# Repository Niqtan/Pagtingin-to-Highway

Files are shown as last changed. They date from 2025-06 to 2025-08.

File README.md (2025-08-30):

# Pagtingin (Obstacle Detecting Glasses)

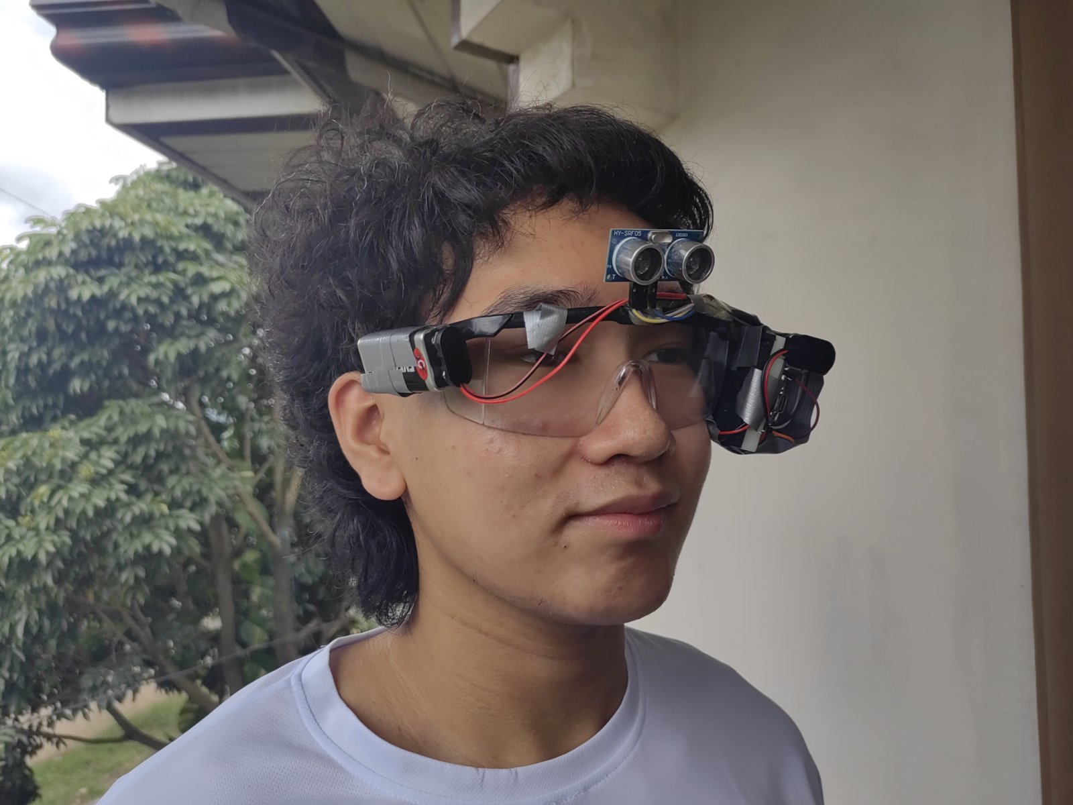
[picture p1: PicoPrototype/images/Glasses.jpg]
Project Wearable

Image 1. Pagtingin Prototype V1

## Prototype Demonstration
https://www.youtube.com/watch?v=mGvRfI-a0dM

# STATUS
Unfortunately, the ordered PCB did not end up working.

## Project Aims

The Pagtingin obstacle detecting glasses aims to help visually impaired people to easily detect obstacles in front of them through innovative glasses. While traditional walking sticks indeed help in detecting obstacles on the ground, they often fail to identify objects at chest or head level, such as low-hanging branches, open cabinets, or protruding signs. 

Hence, Pagtingin aims to aid this limitation and ensure a safe journey of navigation. Whether indoors or outdoors, the device will be able to identify potential hazards through a Time-of-Flight sensor and send real-time audio feedback, which helps users to be much more confident and safe in the user's day-to-day lives.

(+ I wanna try walking blindly sometimes)

Blind person walking happily

Courtesy of Freepik

## PCB Version
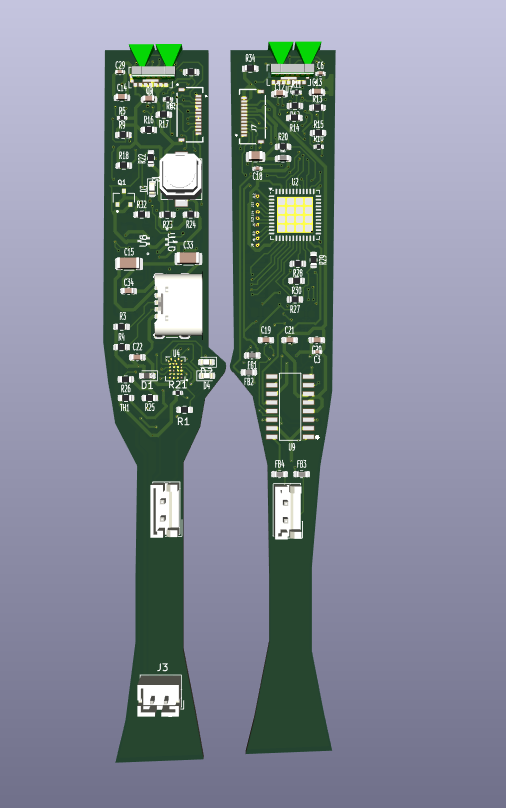
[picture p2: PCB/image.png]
PCB front view

Image 2. PCB Front View

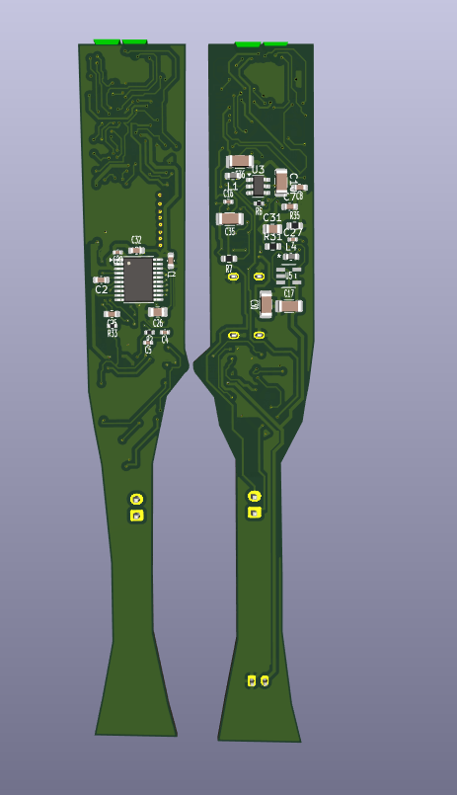
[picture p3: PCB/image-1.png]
PCB Back View

Image 3. PCB Back View

## Panelized Version

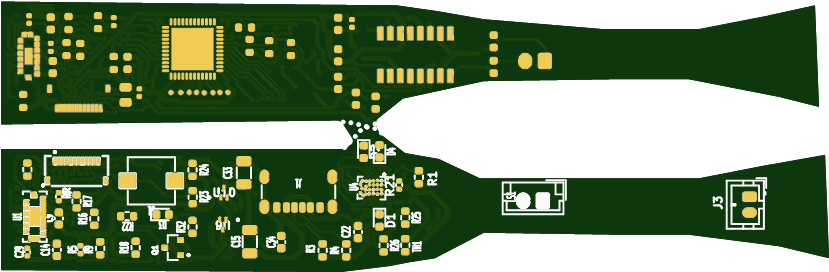
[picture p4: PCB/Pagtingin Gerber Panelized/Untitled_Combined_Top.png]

Image 3. Panelized PCB Front View

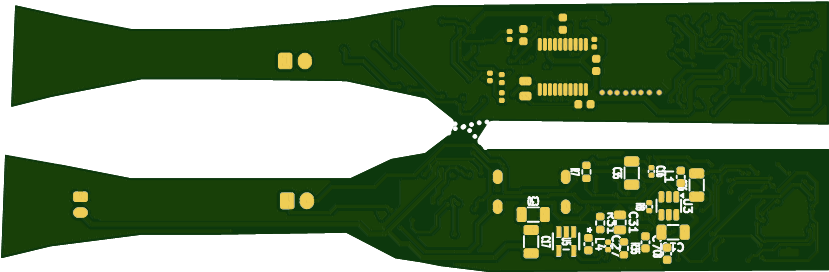
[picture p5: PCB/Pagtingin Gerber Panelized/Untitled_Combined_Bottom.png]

Image 4. Panelized PCB Back View

## CAD

### Glasses Frame

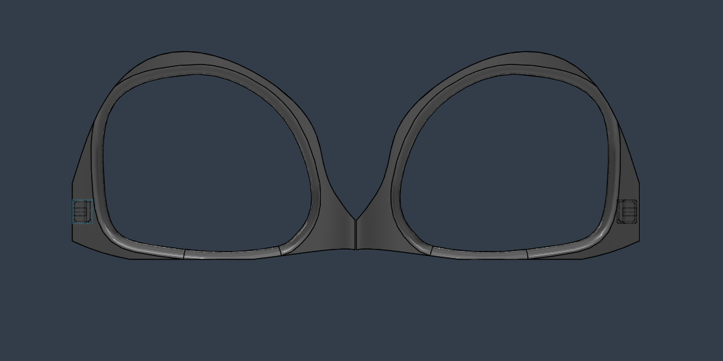
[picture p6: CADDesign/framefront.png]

Image 5. Glasses Frame Front View

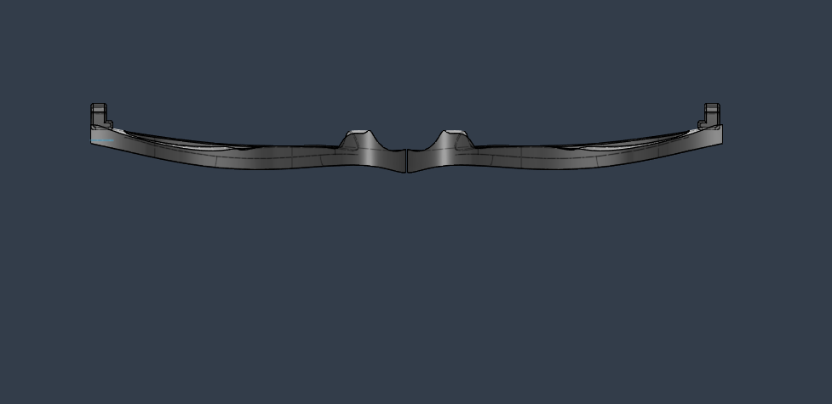
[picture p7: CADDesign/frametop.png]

Image 6. Glasses Frame Top View

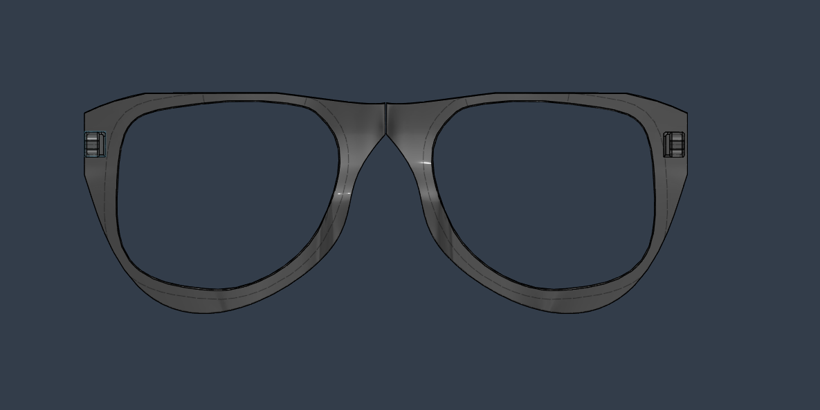
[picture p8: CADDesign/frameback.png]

Image 7. Glasses Frame Back View

### Temples

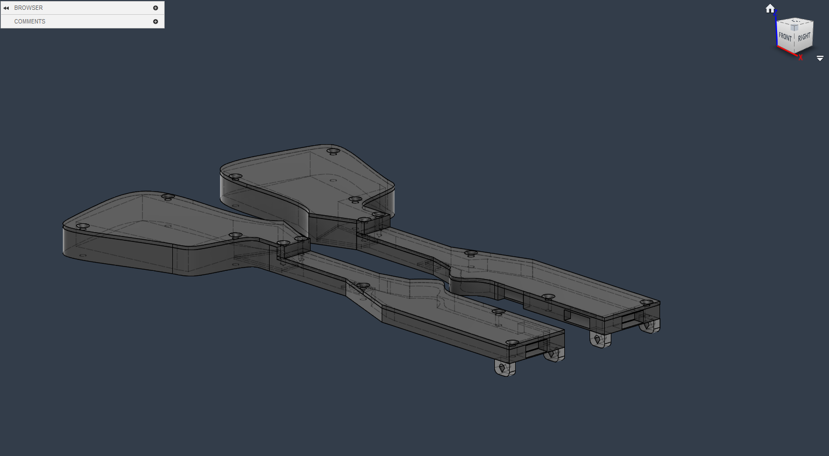
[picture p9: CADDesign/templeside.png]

Image 8. Glasses Temple Side View

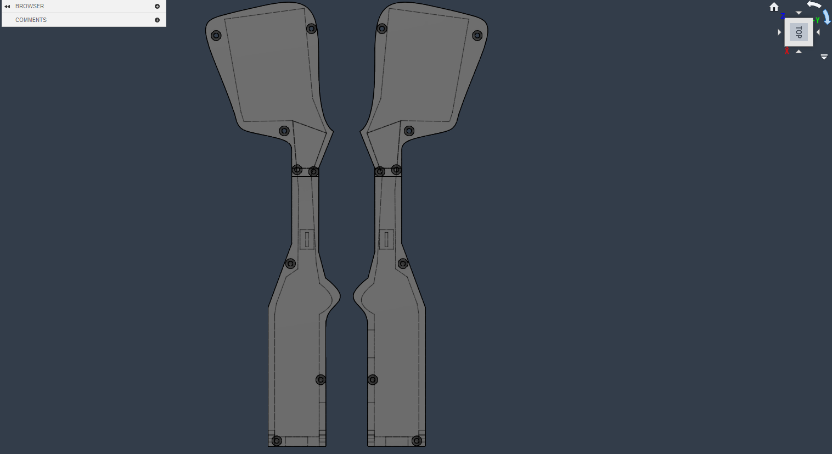
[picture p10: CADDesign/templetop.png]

Image 9. Glasses Temple Top View

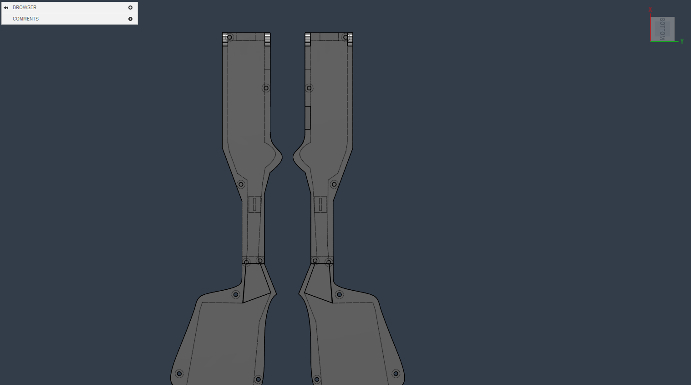
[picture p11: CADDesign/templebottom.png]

Image 10. Glasses Temple Bottom View

## 3D Printing
In terms of 3D printing, it might be better to print this in resin since the glasses frame will require precise dimensions. You may be able to print this in FDM, but it is recommended for the parameters to be as precise as possible.

## BOM
[PagtinginFinal.csv](PagtinginFinal.csv)

## Firmware
Still in progress. You may see previous prototypes in the folder for previous version's firmware. But for the firmware, I am planning to use the ESP-IDF in programming it. I chose the ESP-IDF because it allows full control over the ESP32-PICO-D4's peripherals and such. (also because I wanna challenge myself)

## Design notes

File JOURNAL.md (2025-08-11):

---
title: "Pagtingin"
author: "Niq Suguitan"
description: "A vision without action is called a daydream; but then again, action without a vision is called a nightmare."
created_at: "2025-30-25"
---

DISCLAIMER: I had been working on this project even before Highway. I had a prototype V1 beforehand. However, most of the CAD and PCB Making happened during the duration of Highway.

| Date started: March 17, 2025 

Total hours spenta: 
128 Hours

P.S. These were all my notes taken in Obsidian. Some of them are linked to other pages.

## March

# Entry #0 - 03-17-25
This was the start of me turning my prototype into an actual PCB

Next steps:
- Try to research if I could make the current circuit into  a microchip
-  Sub project (Try to make an earphone in order to make sense of the project)
- Try to somehow integrate electromagnetism with the project 
- Research on how to integrate AI such as Tensorflow Lite and TinyML
- Physics concept
	- Doppler effect
	- Echolocation

Different Research:
- Making microchips:
	- https://www.instructables.com/Make-Your-Own-Microchips/
- Making earphones
	- https://www.instructables.com/DIY-Headphones-2/
- Doppler Effect:
	- https://www.grc.nasa.gov/www/k-12/airplane/doppler.html

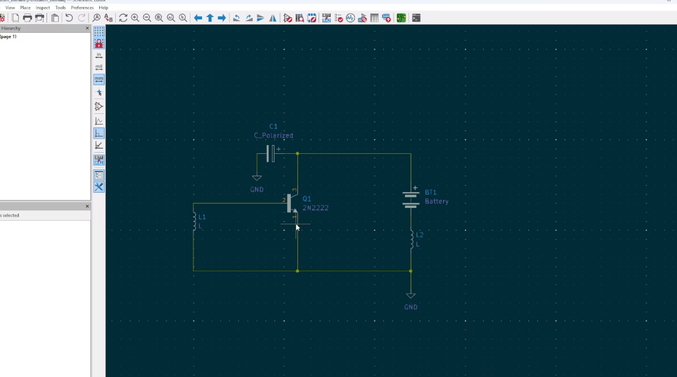
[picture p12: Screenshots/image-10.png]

Image 1. First Steps of my project

Total time spent: 2 hours

# Entry #1 - 03-20-25: Research

Types of Speakers

Headphones tech: driver units
- A driver unit is the most important component in headphones
- A mini speaker in headphones that converts electrical signals through the headphone wire into audible sound

Components of a headphone driver unit
- Magnets
	- Helps improve its sound quality
	- Made of cobalt, ferrite, and more
- Voice coils
	- Produce quality sound feature voice coils made of PCOCC
- Diaphragm
	- Usually, the larger the diameter, the better sound quality seems to be

Types of headphone driver units
- Dynamic drivers
	- Most common and cheapest drivers which use larger diaphgrams
	- Use magnetism and electromagnetism
	- Popular for headphones,, loudspeakers, and earbuds
- Balanced Armature
	- Much smaller and incredibly power efficient
- Planar magnetic
	- Most high-end headphones and earphones use planar magnetics
- Electrostatic
	- Uses an electrically charged diaphragm 
	- Produces exceptional sound quality

Types of Audio Drivers

Bone Conduction Transducer
- Small speaker that does not have a moving cone
- It works electromagnetically since when current flows them magnetic field will expand and contract

Audio exciter
- A sound exciter is a loudspeaker without frame and cone

How does an exciter work?
- Comprised of motor assembly, a voice coil, and a suspension system

Why use an exciter?
- Provides a universal, cost-effective alternative to loudspeakers, allowing for sound reproduction

Where to use an exciter?
- The surfaces themselves will affect how the sound exciter will react in an individual application
	- For example, mounting an exciter onto glass will provide a much different sound than mounting them in a foam of core

Types of exciters
- Coin type
	- Less  than an inch in size
	- Perfect for compact areas where space is limited
	- Oftenly used in toys, monitors, small glass enclosures
- Bone Conducting
	- Converts electrical signal to mechanical vibrations so that it stimulates the bones in the ear
- High Power
	- For increased sound performance
- Extended Mount
	- For projects featuring a larger mounting surface

Are they better than normal speakers?
- It depends.

Total time spent: 3 hours

# References
- https://www.instructables.com/Adafruit-Bone-Conduction-Speaker/
- https://www.daytonaudio.com/topic/excitersbuyerguide

# Entry #2 - 03-21-25: Looking for some components

Microprocessor:
- ESP32-PICO-D4
- Antenna (Need one since the microprocessor does not have it)

Audio Amp:
-  PAM8403DR 
- DAC:
	- PCM5102APWR
- Speaker:
	- MEMS speaker

- [ ] 

Power source
- [[Pagtingin Study -Best Batteries and Use Case - 03-22-25]]

In general:
- SMD (Capacitors, diodes, resistors, etc): [[Pagtingin Study - SMD to use - 03-23-25]]

Sensor:
- TOF Sensor:
	- https://www.mouser.com/datasheet/2/389/vl53l3cx-1799823.pdf

Antenna
- Just add a footprint with a PCB antenna

Debugger and programmer:
- The ESP-PROG with the programmer and JTAG interface

Total time spent: 2 hours

# Entry #3 - 03-22-25: Research on Best batteries and Use case:

Alkaline Batteries
- Usually not rechargable

Rechargable batteries

In general, rechargeable batteries are rechargeable since they have much more chemical reactance. 
- Lithium polymer
	- Requires an extra circuit to prevent overcharging
	- Value is 2500 mAh rated at 3.7V
	- Range of the ESP32-PICO-D4: -0.3V, max 3.6V
	- Range of the TOF sensor chip: 3-5V
	- Range of the DAC chip: 2.5V - 5.5V
	- Range of the Audio AMP: 2.5 - 5.5 V
- NiMH cells
	- Runs on 1.3V or 1.5V

Well for the lithium polymer, this will greatly depend on the needed power of the other components. (Sensor,  audio amp,)

For the glasses project:
- Buck converter to amplify voltages for certain chips

USB IN Module:
- A USB receptacle type C for charging
	- ??
- We need the battery which i chose to be a Li-Po battery
- A battery management chip 
	- TP4056 Works well
	- NTC Thermistor for the TEMP PIN

Individual researches:
- USBs: [[Pagtingin Study -USB C vs Micro USB for Power - 03-22-25]]
- Battery management chip: [[Pagtingin Study -Battery Management Chips - 03-22-25]]
- Power Flow Management: [[Pagtingin Study - Power Management and Flow - 03-24-25]]
- Voltage Supervising & Protection Circuit: N/A

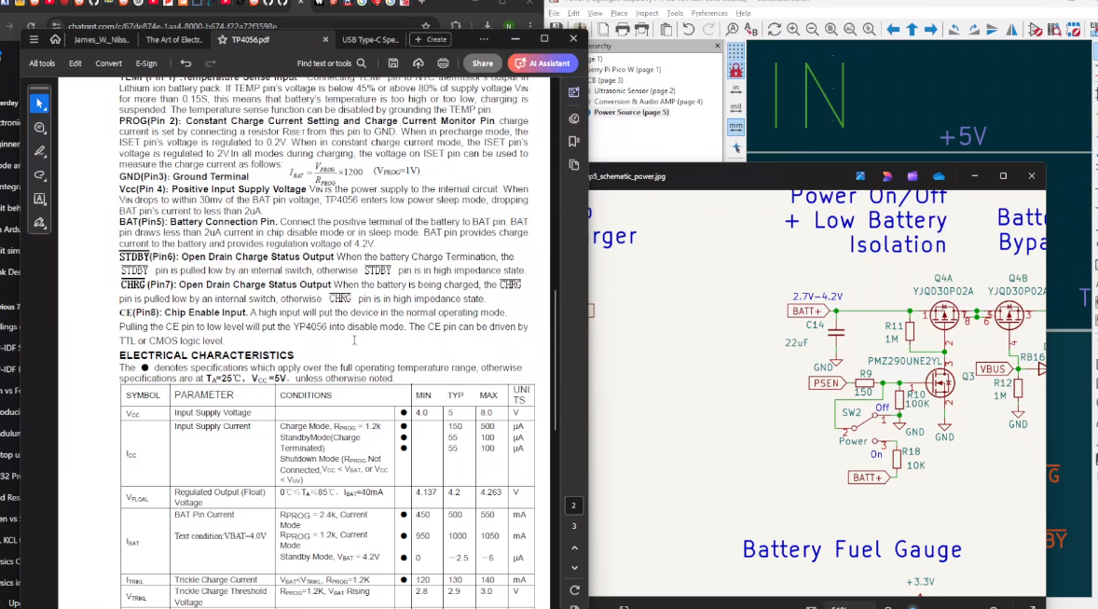
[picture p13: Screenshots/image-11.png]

Image 2. Reading Datasheets

Total time spent: 3 hours

# Entry #4 - 03-23-25: Searching for SMD Components

Resistors
- 0805  resistor
- https://www.digikey.ph/en/products/filter/chip-resistor-surface-mount/52?s=N4IgTCBcDaIAwA44FYQF0C%2BQ

Diode:
- MBR120VLSFT1G ofor the power supply so current doesnt go backwards
- SS34 for the schottky diode

Capacitors model:
- 0603
- https://www.digikey.ph/en/products/filter/ceramic-capacitors/60?s=N4IgTCBcDaIAwDY4GYQF0C%2BQ

Transistor
- MOSFET (This is for the power unit of the circuit)
	- Try out the LFPAK56

Total time spent: 1 hour

### -- INCOMPLETE --

## APRIL

## IMAGES OF APRIL WORK
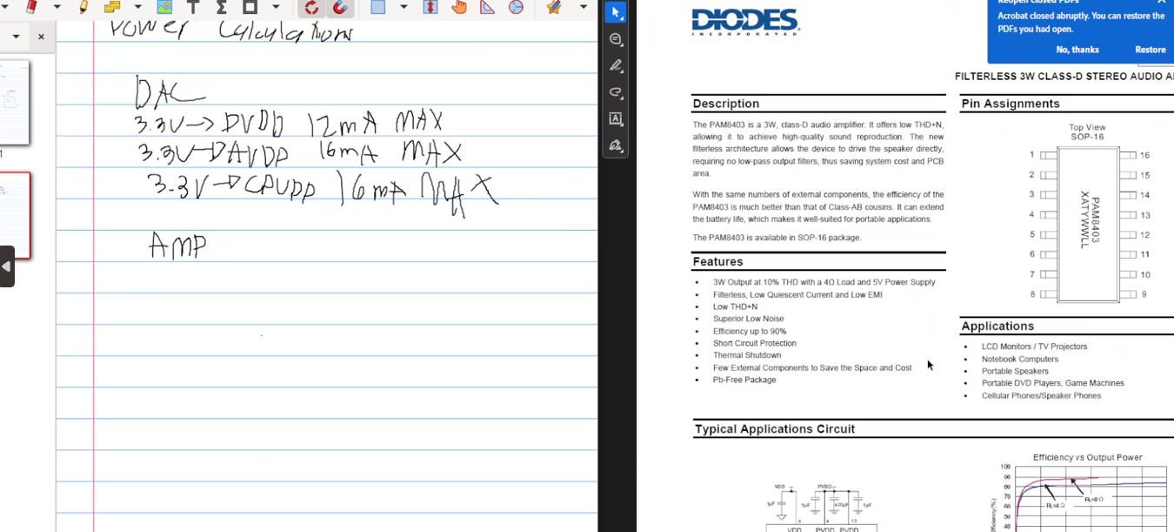
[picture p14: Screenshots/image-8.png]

Image 3. Working with the PAM8403 Audio Amp Chip - 04-06-25

Total time spent: 4 hours

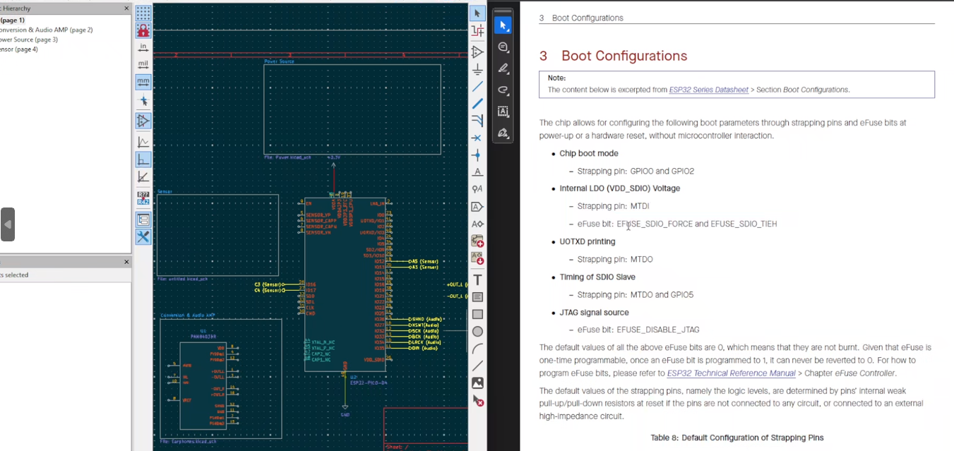
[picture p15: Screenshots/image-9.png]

Image 4. Working with the ESP32-PICO-D4 - 04-07-25

Total time spent: 3 hours

# Entry #5 - 04-13-25: Total and Peak Current of Components Chosen:

ESP32-PICO-D4
- Bluetooth (RF functionality)
	- TX
		- Peak current for transmitting power is 370mA
		- Recommendation: a battery should be able to supply short bursts of at least 400mA
	- RX:
		- Peak current: 120mA
- GPIOs
	- Typical current: depends on what we connect it to
	- Peak current (max current a gpio can source at high): 40mA
	- More than 40mA may damage the pin

PCM5102
- DVDD (powered at 3.3V  and going for 96kHz frequency) (5):
	- 9mA as typical current and 13-15 mA as peak current
	- (6) 96kHz - 9mA
- AVDD / CPVDD (5)
	- 96kHz - 11mA (typical current) and 16mA (maximum current)
	- (6) 22mA (typical current) and 32mA (maximum current)

(5) means its idle (quiescent current)
(6) Means that it is in use

PAM8403
-  Quiescent Current (VDD & PVDD):
	- 5V = 16mA
	- 3.6V = 10mA
	- 3V = 8mA

VL53L5CX
- Quiescent Current (LP IDLE or quiescent current)
	- AVDD - 45 TYP, 300 PEAK/MAX (microamps)
	- DVDD - 0.1 typ, 1 MAX mA
- HP Idle (I2C)
	- LP idle's big brother but not ranging
	- Middle ground between full activity and deep sleep
	- Programmable
	- TYP 1.3 mA, Max 1.6mA - AVDD
	- TYP 2.8mA, MAX 35mA - DVDD
- Active Ranging
	- Typ 45 mA to 50mA (peak) - AVDD
	- Typ 50mA to 80mA (peak) - DVDD
	- Low level voltage
		- 0.54 V
	- High level input voltage
		- 1.13V - 3.6V

Final pick for battery:
Needs 1Ah, 3.7V, and 2C of discharge

It is a balanced ground but to optimize for power:
- Utilize the sleep modes of each component

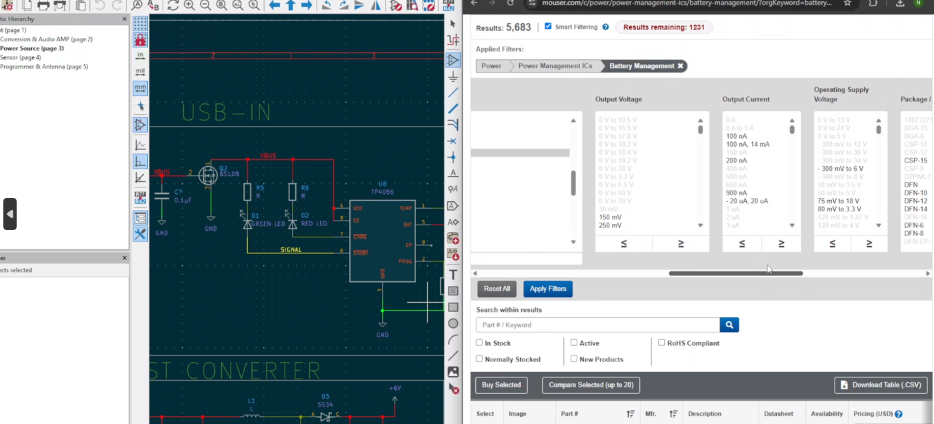
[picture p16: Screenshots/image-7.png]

Image 5. Searching for a better PMIC - 04-20-25

Total time spent: 2 hours

## For May, I mainly did the Firmware but I wasn't able to document it since it was before Highway was announced.

Here are some pictures though (I videod my sessions)
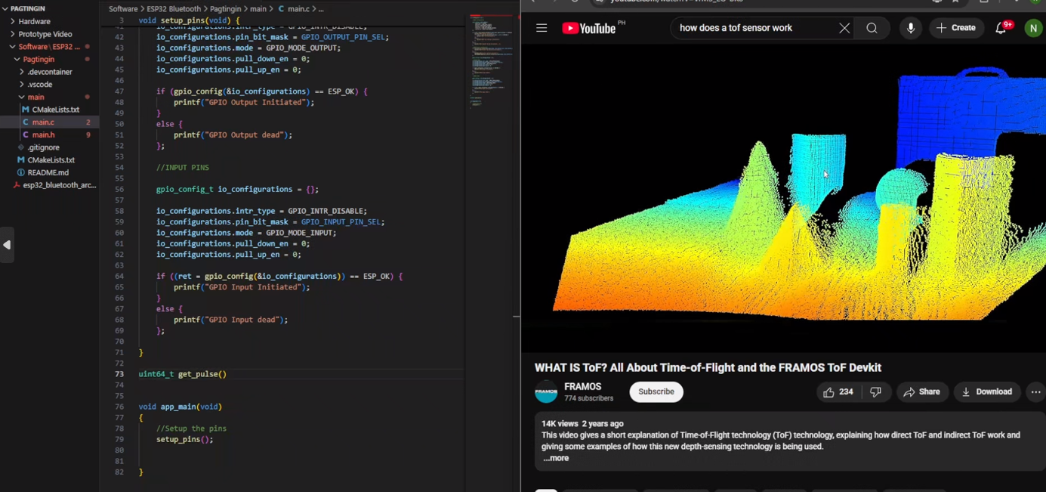
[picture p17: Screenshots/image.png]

Image 6. Learning About TOF Sensor - 05-01-2025
Total time spent: 3 hours

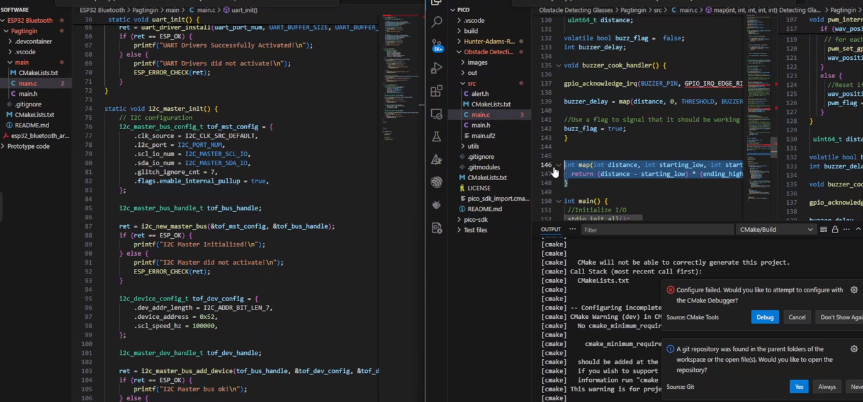
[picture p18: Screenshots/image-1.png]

Image 7. Transferring my Raspbery Pi Pico Code to ESP32 - 05-15-2025
Total time spent: 5 hours

## June: After Highway was announced

# Entry #6 - 06-11-25: Making the PCB and CAD Compliment each other

Today, I have decided to start on the CAD and the PCB

Estimated length and width of the PCB:

Clearance height for the tallest component

Hole positions 

How do you go upon designing glasses?
- Do some side measurements of the glasses' lens
	- Most glasses are actually designed for looks
	- However, the optician, which puts the lens in, they go in and see which lens will fit into the wrap. The wrap is the closest shape of the frame above.
	- We want to make sure that the wrap is going to match the curvature of the lens

However, what type of glasses do the blind actually wear?
- They wear more of the sunglasses style

So I've decided to make sunglasses
- But what style? Specifications? How do we make it enclosed?

Okay here are ideas to make it enclosed:
NaN

How to make the hinges?
- Copy off the sunglasses' hinges and try to make a barrel 

Material for it:
- PETG

To do list:
- Get a rough estimation of the PCB's measurements
- Implement that on the temple
- See what happens for separate prints
- Do the temple design next

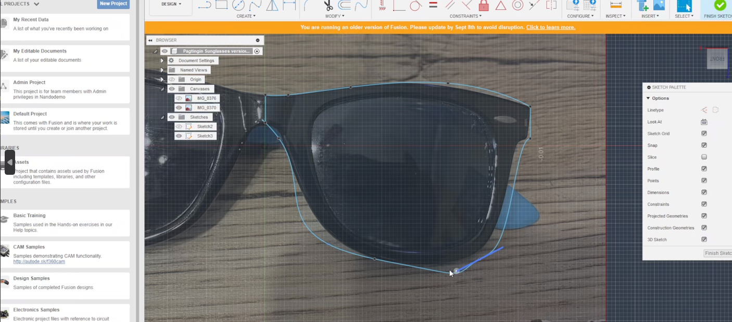
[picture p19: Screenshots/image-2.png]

Image 8. Making the Glasses CAD
Total time spent: 6 hours

# Entry 07 - 06-13-25: Schematic Session 01

Can we connect two TOF sensor chips to the same I2C address line?
- Yes, but they would need to have unique addresses to not have any conflicts in logic

How should i define the shape of the pcb?
- The idea I came up with is that making the PCB shape like the glasses themselves. I would have to find a way to make the 3D printed to be openable somehow. And then, what I would do for my PCB is to make it smaller and be able to fit in the 3D printed glasses naturally while having the shape of the glasses itself, with it being smaller. This way, it allows for much more room and space to place out components evenly throughout the PCB.

No go zones (no electrical connections):
- The hinges or nose pads

Here are the estimated measurements:
- Length of the main rectangular PCB (nose bridge): 0.933 inches -> 24mm
	- Height of the main PCB: 0.267 in
	- Extension (curve of the PCB to both sides of the glasses):
		- 0.56 in only 
- Thickness: 1.0mm

To do list for tomorrow:
- IN the afternoon, try to finish the schematic now
To do list:
- Try to make space for the TOF sensor by making a hole on each of the glasses' sides

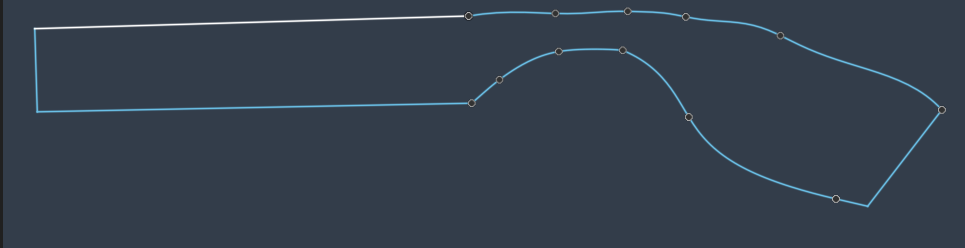
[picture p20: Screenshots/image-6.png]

Image 9. Brainstorming for PCB Shape and Design
Total time spent: 5 hours

# Entry 08 - 06-14-25: Modular PCB Designing & Glasses CAD Design

How do we pick hinges for our glasses?
- Three types of hinges:
	- Flexible spring hinge
		- The spring or flex glasses hinge offers the active wearer a snug fit 
	- Standard or barrel hinge
		- Most common type of hinge
		- Features a series of metal rings (barrels) that fit into each other like a zipper
	- Hingeless design
		- 
- 
Measurements of the hinges
- Recommended hinge type: Standard barrel hinge with 3-5 barrels

So in order to make these hinges:
- Using the measurements of my current frame and the temple, we can determine the measurement of the hinge as well
- I need to make a drawing first of the hinge
	- Draw the recess of the hinge so we know the measurement of what hinge and how to put it
- The type of hinge we're going to be using is a NFW (new facial width) hinge which is much

How do we integrate the hinges now?
- Simple, add a hinges shape integrated in both the frame and the temple (one barrel on the frame, two barrels on the temple)
- Then, we'll just use a metal screw with the right size in order to fit them
	- Measurements of the rectangular pad and hinges in the temple
	- Hole size: M2 Screw
	- Rectangular pad length: 15.745 mm
	- Height of the hinge of the temple: 5.7 mm
	- Length of the hinge of the temple: 3.7 mm

Measurement of the rectangular pad and hinges in the frame:
- 5X5 Square

Next up: Modular PCB designing

Why modular PCB?
- Simply put, having a whole PCB being glasses shaped will not make it sufficient for various reasons:
	- Having one single PCB carrying a complex system is very daunting when the PCB does not work as expected, making debugging harder
	- But how exactly do you make it "modular"
		- In this project, I would define it modular by connecting different PCBs using a Flat Flexible Cable in order to tie all of it together

Refer: [[PCB Making - What is a Flat Flexible Cable (FFC) - 06-15-25]]

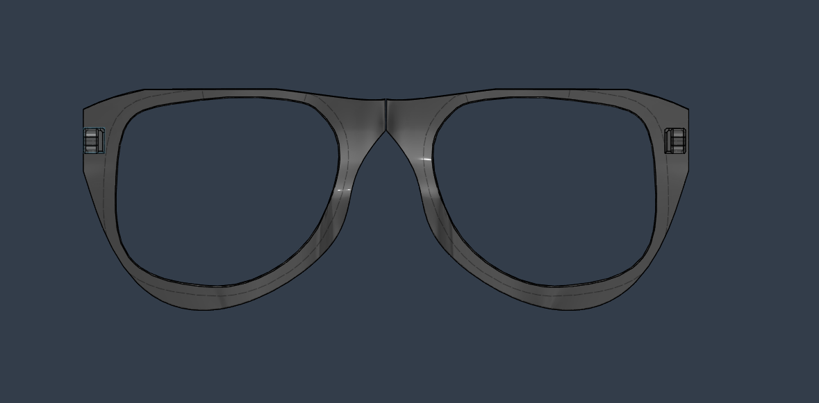
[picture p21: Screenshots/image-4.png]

Image 10. Finished Frame of the Glasses

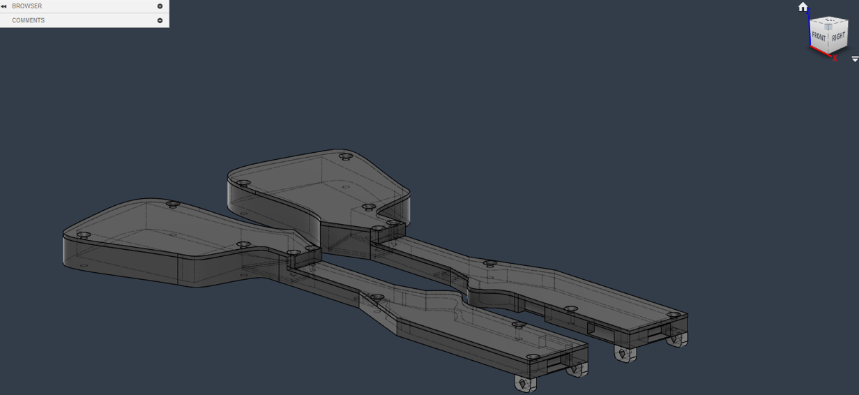
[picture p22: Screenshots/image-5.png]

Image 11. Finished Temple of the Glasses 

Total time spent: 6 hours

# Entry 09 - 06-15-25: Schematic Session 02

For this schematic session:
- Successfully finished the sensor's wiring (fixed the conflict if two different I2C slaves)
- I created a power switch

How to create a power switch? 
- Well what does a power switch mainly do?
	- Controls the power
- For this power switch, I want it to turn on or off (as in the battery will be turned on when this switch gets pressed)

Momentary vs Latching button switch
- Simply put, a momentary push button wont be able to sustain itself, while the latching can

How do we implement this?
- To implement this, we would need to use transistors as logic gates in order for the button to be latching
	- For example, think of the BJT transistor of a NOT gate with a open-collector output. This simply means that whenever the BJT outputs a logic, it will always do the opposite logic, and it will have the effects or output as a BJT transistor would have
- 
So basically, for us to  create a latching circuit, we will need to imagine transistors as logic gates themselves. Using these 3 pins, they can be manipulated in order to logically get what we need. For instance, we used 3 transistors here, one MOSFET and two BJTs, and by using them, we are able to successfully create a circuit where we allow power to pass whenever the switch gives a signal (in which the capacitor also helps via discharging). And in order to continue that, we used the two BJTs in order for us to create an infinite loop to make it on, since it will forever send it to ground.

After that, I went on to double check connections of the power PMIC

To do list:
- Separate the digital and analog planes
- Check up on the audio module, esp. the DAC
- Double check MCU schematic
- Set up values for the inductors on each page

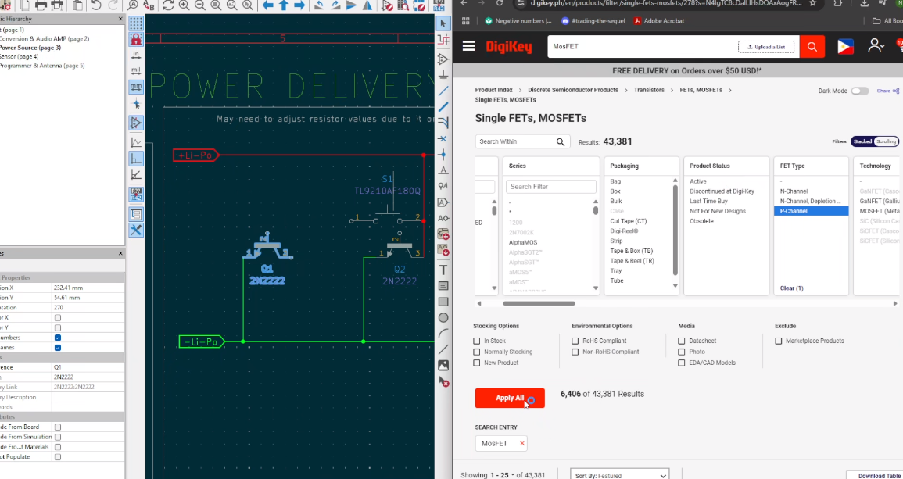
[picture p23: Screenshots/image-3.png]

Image 12. Doing Latching Circuit

Total time spent: 5 hours

# Entry #10 - 06-17-25: Schematic Session 03

For this schematic session, I was able to:
- Finish up the boost converter's values
	- Using the given formulas and such, I was able to find out values that would compliment by power supplu
- Recheck the antenna and put some values
- Recheck the audio part and check DAC connections
- Added ferrite beads to the PAM8403

Getting started with KiCad's Testing:
What are the different types of test?
- OP - Operating Point Analysis
	- Calculates the DC operating point of all nodes and devices in the  circuit
- DC - DC Sweep analysis
	- Sweeps a DC source over a range and records circuit response
- TRAN - Transient Analysis
	- Simulates the circuit over time, showing how voltages and currents change dynamically

Then I assigned footprints and stuff

To do list:
- Debugging the schematic and finding a way to simulate all of this stuff
- Try to start making PCB

Total time spent: 3 hours

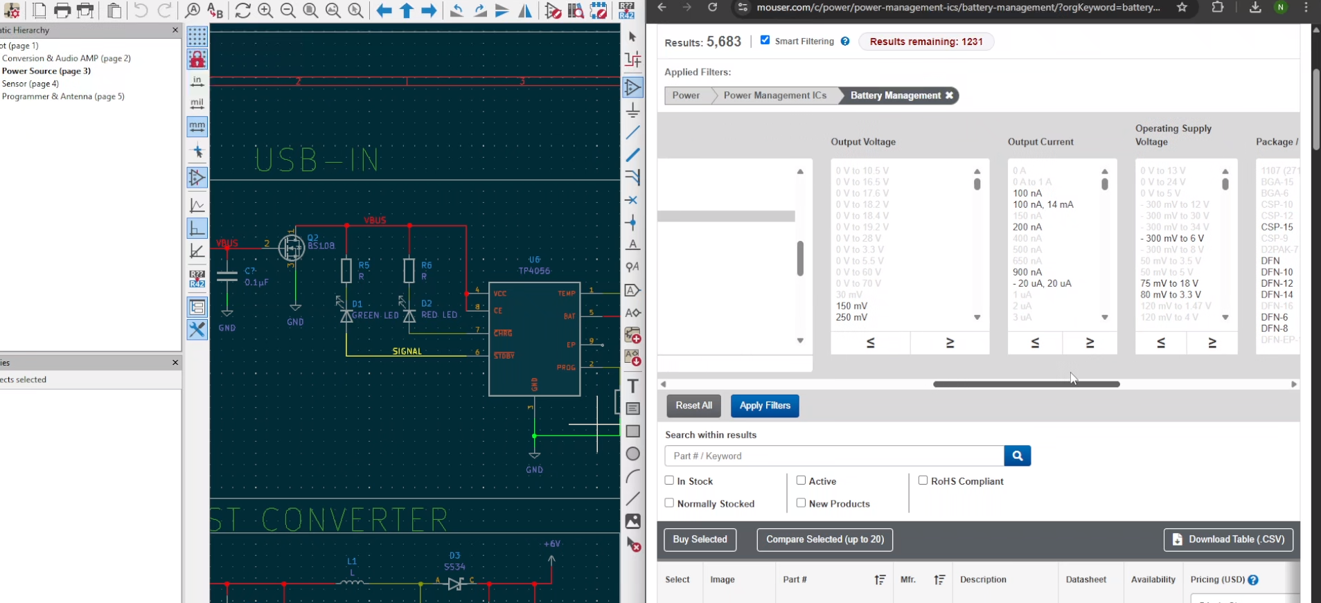
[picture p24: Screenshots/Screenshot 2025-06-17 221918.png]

Image 13. Polishing Schematic

# Entry 11 - 06-18-25: PCB Making Session 01

What type of PCB will we use?
- A double layer PCB, with a front and back side.

Best type of surface finishes?
- What is a surface finish?
	- It is a intermettalic joint between the bare copper of the solderable area of the PCB and components
	- Allows for the PCB's copper of the substrate to not be oxidized

Next we set-up the constraints according to the manufacturer's details

Reminder: Select footprint for battery of connector

Introduction to Multiboard PCB Design: [[Pagtingin Study - Introduction to Multiboard PCB Design - 06-18-25]]

I ran into a problem though.
- Since Im planning to make this into separate PCB, that means I need to make them connected somehow 
	- For that, I used a FFC connector and FFC in order to solve that problem.
	- So the amount of pins needed depended on these signals:
		- Power (3.3V, 5V)
		- Analog Power (3.3V)
		- Ground
		- Analog Ground
		- SDA 
		- SCL
		- Audio Lines (OUTL and OUTR)

Another problem I ran into:
- Was that my shape and measurements wasnt exactly right
	- Revised measurements: 
- Sometimes I confused height for length and such
- Also I havent thought about making it openable

Also I had concerns about heating and the battery exploding, here is what I thought of:
- Thermal Relief on the PCB
	- Add large copper pours esp on GND and VDD planes
	- Add thermal vias to spread heat across layers
- Place hot parts near air gaps
	- Put the boost converter to the outer wall of the temple
- Use exposed pad footprint

Then I started implementing the FPC connector

Total time spent: 6 hours

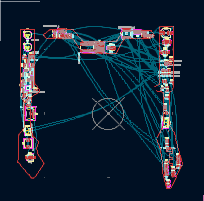
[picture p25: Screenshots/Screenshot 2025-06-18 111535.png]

Image 14. Layoutting the PCB

# Entry 12 - 06-19-25: PCB Making Session 02

When implementing the FPC connector, I noticed the two PCB boards needed FPC connectors for the components they had needed the signals they required

The first FPC connector (Power Supply PCB)
- SDA 
-  SCL
- Audio Lines (OUTL and OUTR)
Total around 4 pins

Pitch: 0.5mm

The second FPC Connector (The Main functionality PCB)
- Power (3.3V, 5V)
- Analog Power (3.3V)
- Ground
- Analog Ground
- Total around 5 PINS

	Pitch: 0.5mm

Now getting into layoutting problems
- The problem with layoutting, is that since this is a small PCB, I had to check if electrolytic capacitors were working, which they were not
- I also revised the shape and measurements to be  according to the CAD

Connecting the components together
...

Basics of Vias:  [[PCB Making  - Via Basics - 06-19-25]]

Total time spent: 6 hours

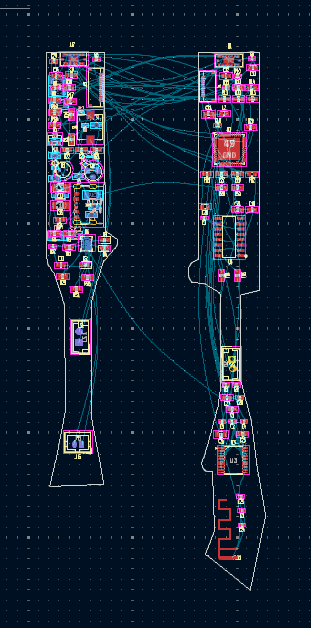
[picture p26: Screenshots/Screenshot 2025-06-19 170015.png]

Image 15. More Progress on Connecting Traces

# Entry 13 - 06-20-25: PCB Making Session 03

Anyways for ths PCB Making Session, I had to research up on mouse bites (breakaway tabs) in order for my two PCBs to still be separated but manufactured into one PCB

What is V-Score?
- Involes adding grooves for easy breaking later on

Also, since I needed to program my MCU, I needed pogo pins
- Pogo pins: 

Also some polishing was done:
Width changed to 15.250 mm
Length is still close to 103-105 mm

Total time spent: 7 hours


Image 16. Almost done layout and PCB

# Entry 14 - 06-24-25: Finished PCB and CAD




Total time spent: 9 hours

# Entry 15 - 06-27-25: Making a prototype and the firmware!

For today, I've tried making progres on making the prototype of the PCB version on a breadboard. I've used the breakout boards for each chip so that it closely aligns with what I'm making.

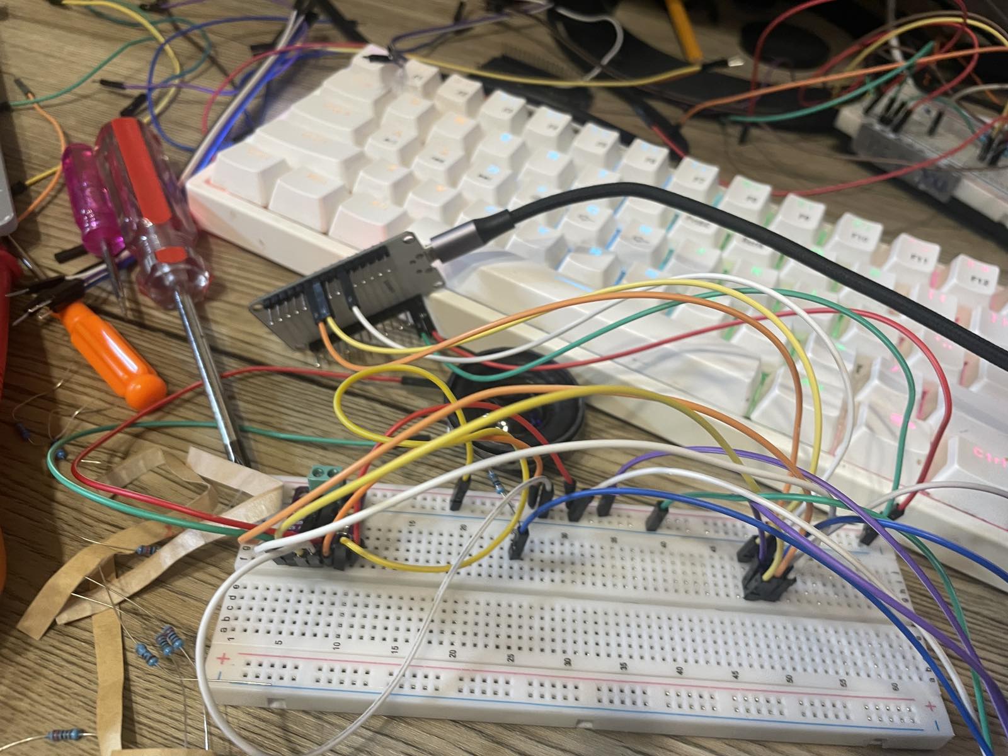
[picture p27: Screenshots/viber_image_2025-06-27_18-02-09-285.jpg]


Image 17. Unit testing the audio part of the system 

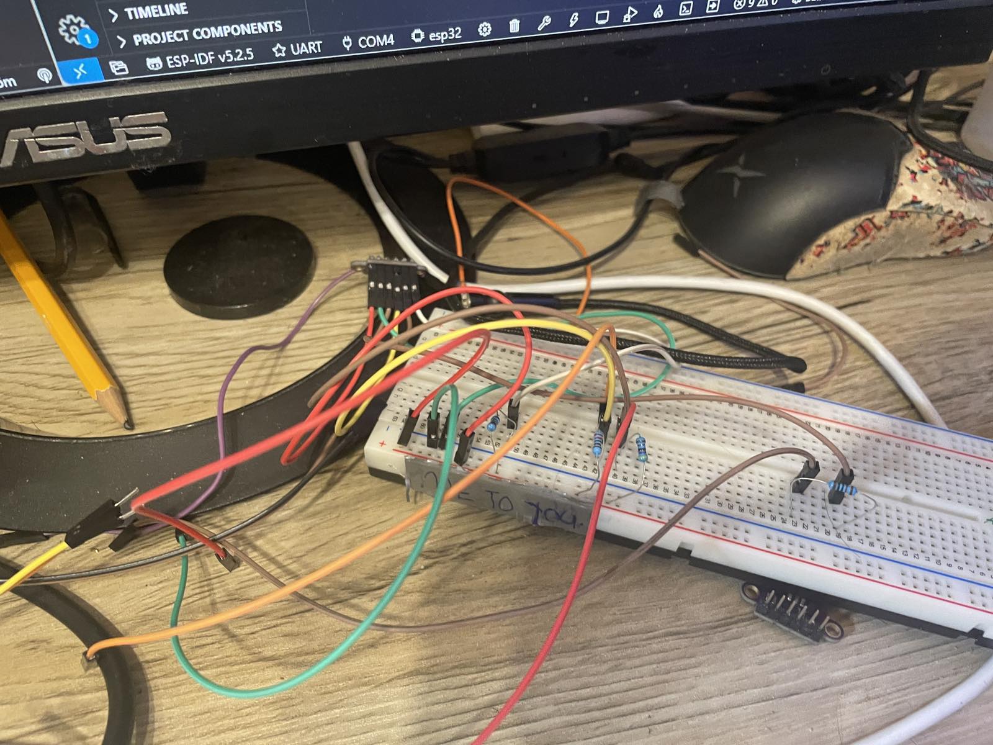
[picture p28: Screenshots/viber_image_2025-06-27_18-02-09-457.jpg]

Image 18. Unit testing the sensor part of the system

Besides making progress on the prototypes, I've also been making progress on the firmware. I estimate it around 75% done now that the sensor and audio part is done.


Image 19. Firmware Progress

All im missing is to implement a Finite State Machine (FSM) model which is a core to this system.

Here's a to do list:

- Create a FSM model
    - Include states such as IDLE, ALERT, MUTE

Power Management:
- Sleep modes (when idle)

Decision-making:
- Make the ditances much more robust
    - Apply thresholds for triggering different distance categories

Interrupts:
- Override current actions with emergency

User Feedback
- The LEDs

Total hours this session:
5 hours

# Entry 16 - 06-30-25 - Panelized Board and Polished CAD for PCB, and ordering PCB w/ Assembly

For today, I've mainly went around panelizing my board and polishing my CAD for ordering.

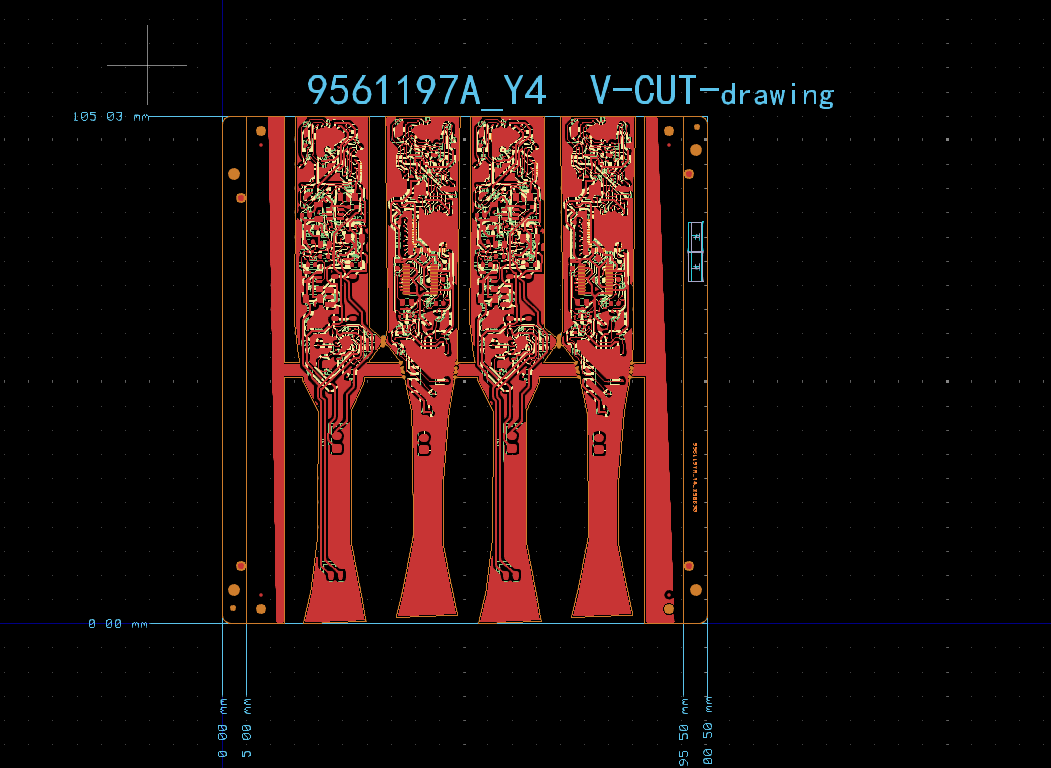
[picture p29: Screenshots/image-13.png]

Image 20. Panelized PCB

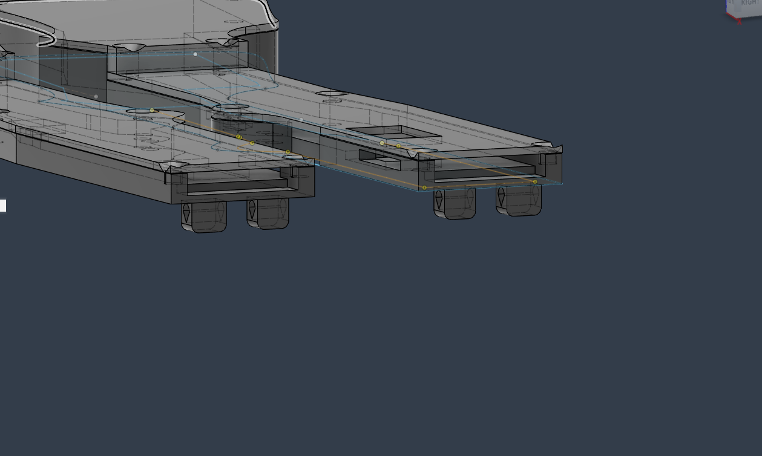
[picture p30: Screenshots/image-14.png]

Image 21. Polished CAD Hinges

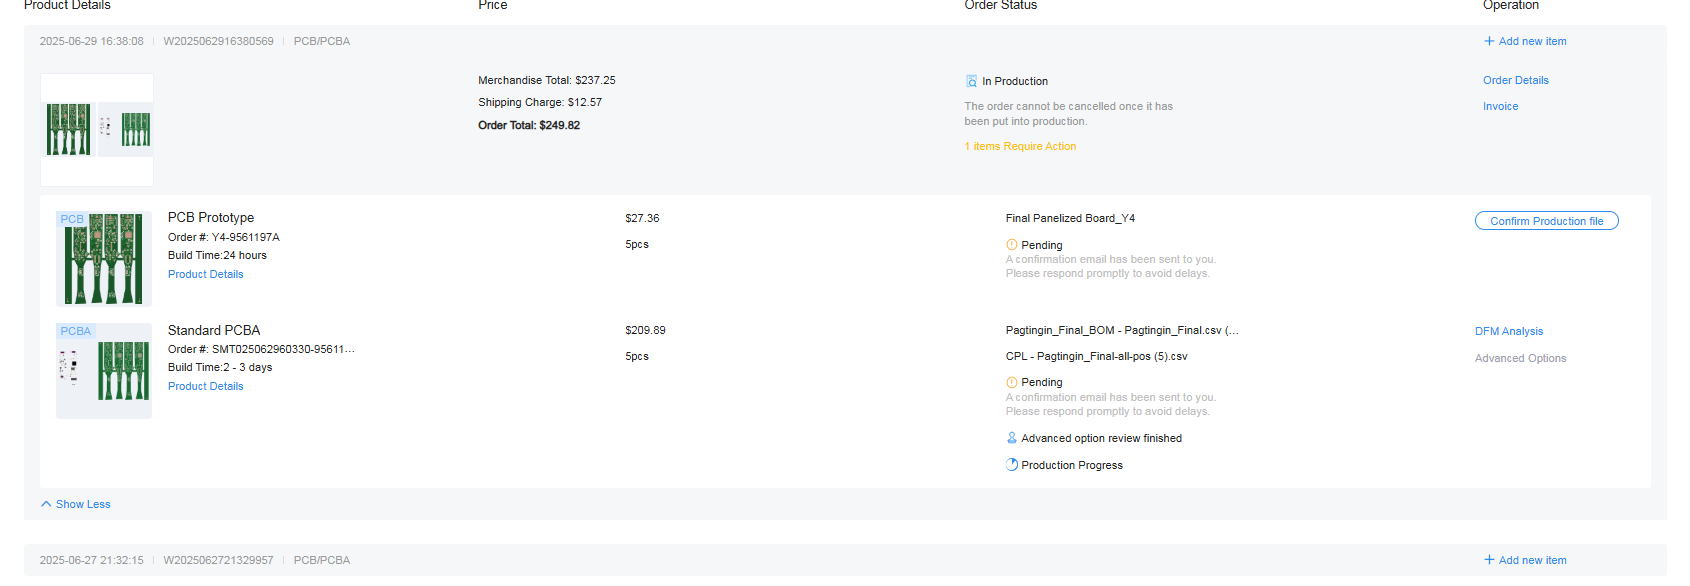
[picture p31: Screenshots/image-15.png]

Image 22. Ordered from JLCPCB

Besides that, I've also ordered from other manufacturers who I need parts from. Next part would be building the project.

Hours spent: 8 hours

# Entry 17 - 07-02-25 - Wrapping up firmware and finishing up Unit Testing

For yesterday and today, I've been mainly wrapping up the firmware. For the firmware, I've added an algorithm known as the Finite State Machine (FSM). I've added states to my program so that it can have its own sort of system.

I've mainly added:
- State system (IDLE, ALERT, MUTE)
- Accomodation of two TOF sensors (2 I2C channels)

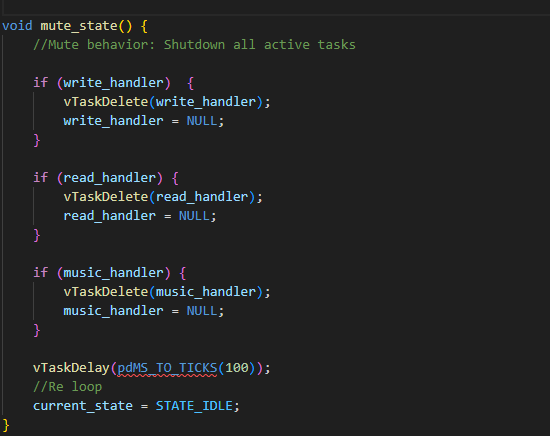
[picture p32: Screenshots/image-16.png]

Image 23. Added more Firmware progress

Also, I've mainly wrapped up my unit testing (or prototyping) of each functionality of the Obstacle Detecting Glasses (Sensing and outputting beep sounds) on breadboards. See the firmware of the unit testing.

Hours spent: 7 hours

# Entry 18 - 07-09-25 - Soldering remaining parts of the PCB
Yay! The parts finally arrived

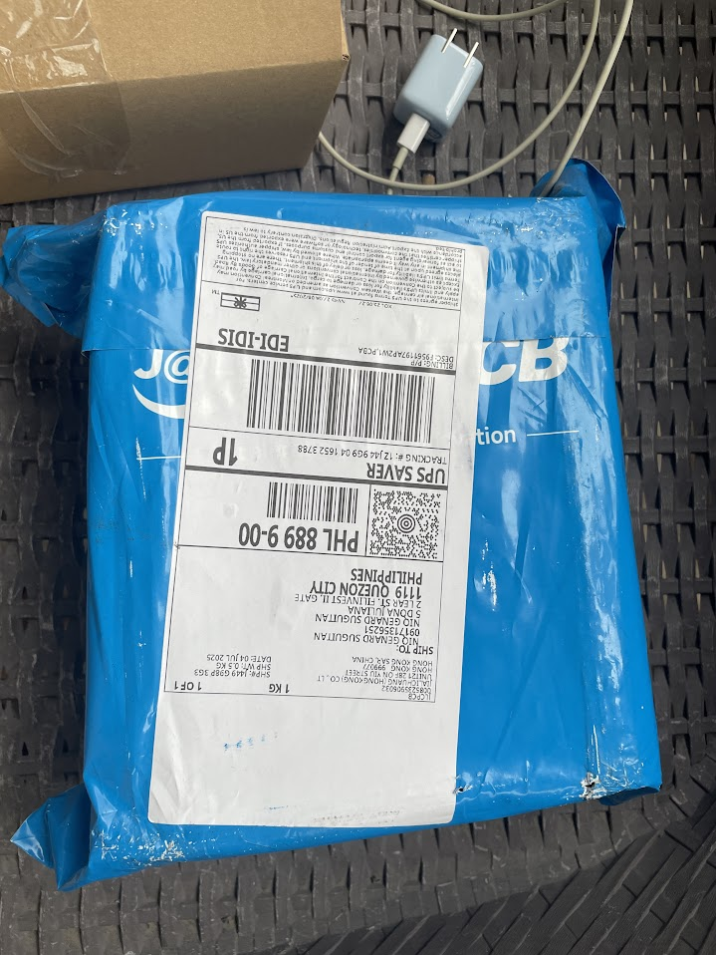
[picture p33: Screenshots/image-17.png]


Before going to Undercity, I just settled with just trying to solder all the missing parts. Not yet complete though!

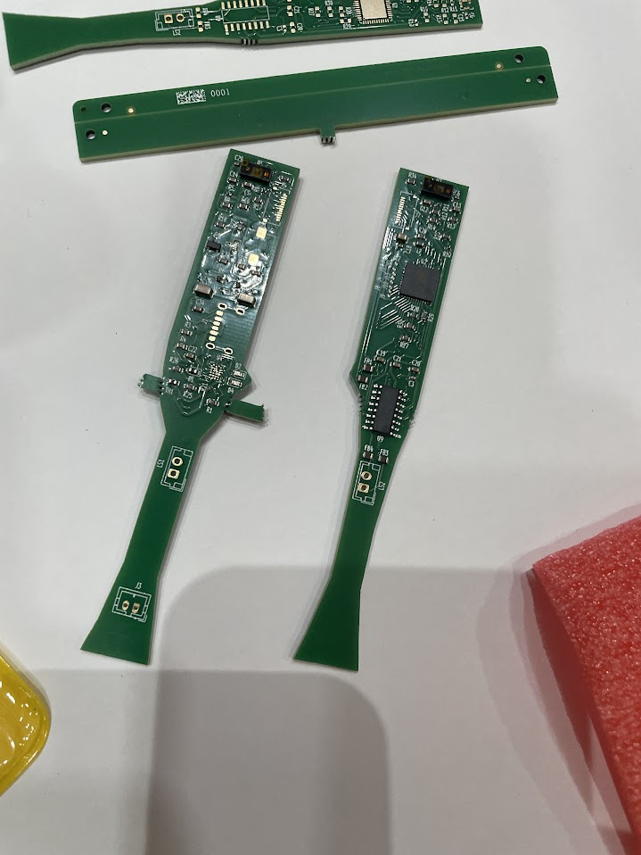
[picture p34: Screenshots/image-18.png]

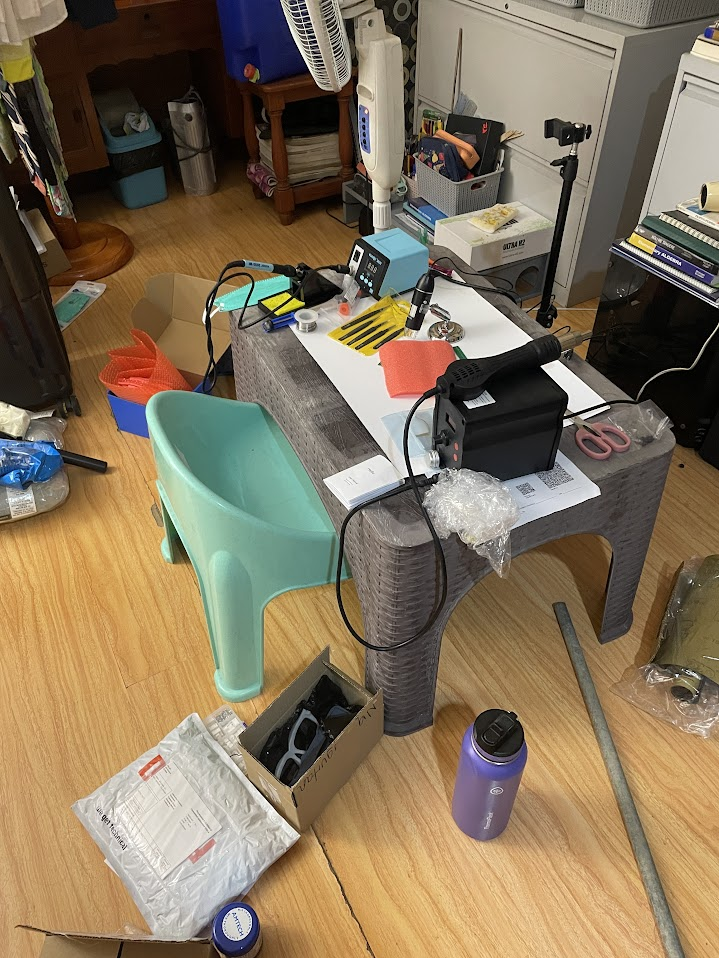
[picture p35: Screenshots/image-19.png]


Images 23-26. Parts and Soldering!

Total hours spent: 3 hours

# Entry 19 - 07-27-25 - Finished Soldering em!
Sorry this journal took so long! Been doing so much stuff. Finished soldering everything!


Image 27. Finished Soldering!

Total hours spent: 4 hours

# Entry 20 - 07-28-25 & 07-29-25 - Failures! Oh Failures!
Welp, so in this journal, I realized how cooked I am. 

Apparently the POGO pins I ordered werent a good fit for my ESP32-PICO-D4's pins.
They are actually too small, literally.


Image 28. Small holes too much

The reason why I actually need these pins is because I want to be able to program the chip using the ESP-PROG, which I didn't know actually had a FPC cable for a FPC connector lmao. (they didn't sell that in the digikey page).

I tried getting away with some copper strips, but then I knew that was a bad idea since if they touched each other close enough, it would potentially short circuit.

Image 29. Trying out copper strips

Yeah so even if I knew  that, I tried it. Guess what? It didn't short cirucit but
the firmware just didn't flash as well. That means the TX and RX pins are having some major issues.

Uhh,, so basically what I thought of was using enamel coated wires or magnetic wires since they don't really conduct with each other. I hope it goes well lol.

Total hours spent: 7 hours

# Entry 21 - 07-30-25 - Wow more errors

Lowkey, for this, I don't think i ain't comin back anymore.

I found another, very critical error with my design. I actually findled with the NPM1100-CAAA-R7's sizes so that I could fit in vias and traces. Hence, when I actually got the PCB, it looked like that. Guess what, the NPM1100-CAAA-R7 didn't fit when I tried to reflow it.... HAHAHAHA im cooked.

Here's what it looks like:

Image 30. Microscoped image of the error

Here I thought, after testing continuity of my PCB (which was mostly correct), I would finally get this working. But nah. Guess we ain't ballin.

Im gonna try putting some wires into it with enamel.

Total hours spent: 3 hours

# Entry 22 - 08-03-25 - Flashing the firmware!

So I've finally connected the enamel wires to the respective pins of the ESP-PROG. 


Image 31. New Setup with Enamel Wires

However, still shows an error that the serial data cannot be received or something. I'm pretty sure its just with the wiring.

Bad news:

My charging module, the NPM1100-CAAA-E-R7 officially cannot be connected to the PCB (see Entry 21: Image 30). The problem was the footprint which I findled with the sizes and stuff before sending it off to JLCPCB. Now, even after searching for solutions on how to connect those pads, i just can't seem to find a way. Deadbugging would be a waste of time since the enamelled wires would quickly be severed considering how thin it is. Hence, I decided to give up on that and not connect any charging modules. 

Now, are there any side effects if I don't connect my charging module? For one, of course charging the battery would be risky since we wouldn't have any indicator at all, as well as protection. However, that doesn't mean that the system will not work. Good thing I did was that I COMPLETELY separated the regulators and DC-DC converters. That basically means that we absolutely can work this out if I don't take all the power from my battery.

Honestly after this, if it flashes, I think that's pretty much the last stage of this project.

Total hours spent: 5 hours (w soldeirng)

# Entry 23 - 08-10-25 - Problems and Resolving

So more problems still come huh? Well this one, I had problems with the FPC connector and the cable. Simply put, I ordered the wrong FPC connector which had the wrong features (it was supposed to have ZIF but it turned out to be solder retention). Yeah, so i tried that for a couple of days. Nope, didn't work out.


Image 32. FPC connector and Cable not fit together

But anyways the solution I had in mind for that was that, what if I just connected each pin to each other individually with enamel wires. Yes, at the cost of a faulty design, we might be able to get this working, which i would love to see. So that is what I did. You can see the picture I attached.

Honestly, this is probably my last resort then I could go on FINALLY testing my firmware.


Image 33. NewER Setup with Enamel Wires

Total hours spent: 6 hours

# Entry 24 - 08-11-25 - No serial data received.

AHHHH!!! I keep having the same problem!!



What does it mean to have your serial data rejected? Since I'm working with the ESP-PROG and the ESP32-PICO-D4 Chip, I obviously did not think this out. Of course flashing on a chip will be different on a dev board. But I swear I literally connected the important pins and then connected it in the PROG tab.



Even connecting power doesn't seem to solve the issue! I've been testing stuff with my multimeter. Guess what? Even my boost converter has problems. For some reason, it only outputs 3V even though I configured it mathematically to 5V.



There are honestly too much problems.

# The Downfall

Welp, I guess I realized it quite a bit late. I guess this all started with this one error:

"COM4 failed to connect: Failed to connect to Espressif device: No serial data received.
For troubleshooting steps visit: https://docs.espressif.com/projects/esptool/en/latest/troubleshooting.html
Serial port COM3
Connecting.......................
COM3 failed to connect: Failed to connect to Espressif device: No serial data received.
For troubleshooting steps visit: https://docs.espressif.com/projects/esptool/en/latest/troubleshooting.html"

I thought I just needed to power it up. Perhaps using enamel wire? Huh? not working????????????????????????????????????.

...

..

.

I didn’t realize at the time that by switching the physical positions of the pads in the footprint, I was also changing the actual pin assignments of the MCU.
I had this mistaken assumption that the manufacturer would somehow “internally” connect my rearranged pads to the correct pins on the chip.



This decision ended up being the breaking point of my PCB.
By tinkering with the footprint layout, I unintentionally rerouted signals to the wrong pins entirely.
In short, my footprint changes didn’t just make tracing easier, they fundamentally altered where every trace connected, which made the whole design unusable.

# Project Conclusion

Welp, I guess this is the end. This project reached a hard stop due to a critical design error in the PCB footprint for the ESP32-PICO-D4. In an attempt to make routing easier, I rearranged the physical pad positions in the footprint.

# Key Lessons
1. Never alter the functional pad order of an MCU footprint.

2. Cross-verify pin mappings between the schematic symbol and footprint before starting PCB layout.

# Next Steps
- Redesign the PCB without ALL of the footprint mistakes
- Add test pads and FPC connectors for future programming and debugging

Total hours spent: 3 hours

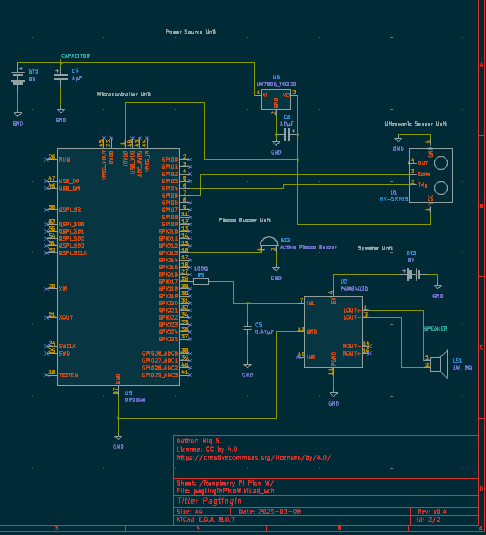
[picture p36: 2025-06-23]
PicoPrototype/images/Circuit.png

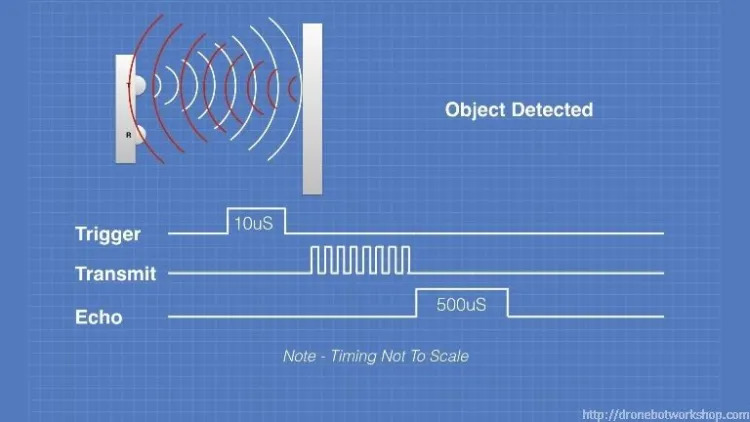
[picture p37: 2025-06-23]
PicoPrototype/images/download.jpeg

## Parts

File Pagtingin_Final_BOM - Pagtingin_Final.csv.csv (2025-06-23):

Comment | Specific Part | Designator | Footprint | LCSC Part # | Total
1µ Unpolarized capacitor | CL03A105MQ3CSNC | C1,C7,C8,C9,C12,C13,C14,C19,C20,C21,C22,C25,C32 | C_0603_1608Metric |  | $1.00
2.2µ Unpolarized capacitor | CL03A105MQ3CSNC | C2 | C_0603_1608Metric |  | $0.08
0.1µ Unpolarized capacitor, small symbol | CL03A105MQ3CSNC | C3,C6,C18,C28,C29 | C_0402_1005Metric |  | $0.39
22n Unpolarized capacitor |  | C4,C5 | C_0402_1005Metric |  | $0.20
10µ Unpolarized capacitor | CL21A106KOQNNNG | C11,C26,C31 | C_0805_2012Metric |  | $0.24
22µ Unpolarized capacitor | CL21A106KOQNNNG | C10, C15,C17,C33,C36 | C_1206_3216Metric |  | $0.48
3.8n Unpolarized capacitor | GRM155R71H392JA01D | C16 | C_0402_1005Metric |  | $0.10
4.1p Unpolarized capacitor |  | C27 | C_0402_1005Metric |  | $0.10
33µ Unpolarized capacitor | CL21A106KOQNNNG | C30,C35 | C_1206_3216Metric |  | $0.16
4.7µ Unpolarized capacitor | CL03A105MQ3CSNC | C34 | C_0603_1608Metric |  | $0.08
PTVS17VS1UR,115 Zener diode | PTVS17VS1UR,115 | D1 | D_0603_1608Metric |  | $0.24
XL-1608VRC-06 Light emitting diode | XL-1608VRC-06 | D2 | LED_0603_1608Metric |  | $0.02
XL-1608PGC-06 Light emitting diode | XL-1608VRC-06 | D3,D4 | LED_0603_1608Metric |  | $0.04
MAF1608FAD151CT000 Ferrite bead | MAF1608FAD151CT000 | FB1,FB2,FB3,FB4 | L_0603_1608Metric |  | $1.20
USB_C_Receptacle_PowerOnly_6P USB Power-Only 6P Type-C Receptacle connector | GCT USB4130‑GF‑C | J1 | USB_C_Receptacle_GCT_USB4125-xx-x-0190_6P_TopMnt_Horizontal |  | $0.64
USE-702528-500PCBJST Generic connector, single row, 01x02, script generated | USE-702528-500 | J3 | JST_PH_B2B-PH-K_1x02_P2.00mm_Vertical |  | $5.50
CPG-13-SMT-B | CPG-13-SMT-B | J4,J8,J9,J10,J11,J12,J13,J14 | SAMESKY_CPG-13-SMT-B |  | $4.48
FFC2B28-12-G | FFC2B28-12-G | J5,J7 | GCT_FFC2B28-12-G |  | $0.78
2.5µ Inductor | AOTA-B160808S2R2MT | L1 | L_0603_1608Metric |  | $0.26
10µ Inductor | MLZ1608M100WT000 | L2 | L_0603_1608Metric |  | $0.10
2.2µ Inductor | AOTA-B160808S2R2MT | L4 | L_0603_1608Metric |  | $0.26
CS15-01P280-02-1 Speaker | CS15-01P280-02-1 | LS1,LS2 | JST_EH_B2B-EH-A_1x02_P2.50mm_Vertical |  | $4.44
2N7002BK 0.2A Id, 200V Vds, N-Channel MOSFET, 2.6V Logic Level, TO-92 | 2N7002BK | Q1 | TRANS_PMV130ENEAR |  | $0.30
10k Resistor | CPF-A-0603B10KE | R1,R19,R20,R25,R26,R27,R28,R29,R30,R34 | R_0603_1608Metric |  | $2
1k Resistor | CPF-A-0603B1K0E | R2,R33 | R_0402_1005Metric |  | $0.42
56K Resistor | CPF-A-0603B56KE | R3,R4 | R_0603_1608Metric |  | $0.42
2k2 Resistor | CPF-A-0603B2K0E | R5,R6,R10,R11 | R_0402_1005Metric |  | $0.80
47k Resistor | CPF-A-0805B47KE | R7,R9,R12,R13,R14,R15,R16,R17,R18 | R_0603_1608Metric |  | $1.89
4k7 Resistor | CPF-A-0402B4K7E | R8 | R_0402_1005Metric |  | $0.20
1k5 Resistor | CPF-A-0603B1K5E | R21 | R_0402_1005Metric |  | $0.21
10K Resistor | CPF-A-0603B10KE | R22,R23 | R_0603_1608Metric |  | $0.40
700K Resistor | CPF-A-0805B680KE | R24 | R_0603_1608Metric |  | $0.21
240k Resistor | CPF-A-0603B237KE | R31 | R_0603_1608Metric |  | $0.21
100k Resistor | CPF-A-0402B100KE | R32 | R_0603_1608Metric |  | $0.20
53.6k Resistor | CPF-A-0603B56KE | R35 | R_0603_1608Metric |  | $0.21
TL9210AF180Q | TL9210AF180Q | S1 | SW_TL9210AF180Q |  | $0.70
NCU18XH103F6SRB Temperature dependent resistor, negative temperature coefficient | NCU18XH103F6SRB | TH1 | R_0603_1608Metric |  | $0.14
VL53L5CXV0GC_1 | VL53L5CXV0GC_1 | U1,U7 | XDCR_VL53L5CXV0GC_1 |  | $17.12
ESP32-PICO-D4 RF Module, ESP32 SoC, Wi-Fi 802.11b/g/n, Bluetooth, BLE, 32-bit, 2.7-3.6V, external antenna, QFN-48 | ESP32-PICO-D4 | U2 | QFN-48-1EP_7x7mm_P0.5mm_EP5.3x5.3mm |  | $6.79
TLV61070ADBV Boost Converter, 2.5A switch current limit, 2.2-5.5V Output Voltage, 0.5-5.5V Input Voltage, SOT-23-6 | TLV61070ADBV | U3 | SOT-23-6 |  | $0.44
NPM1100-CAAA-R7 | NPM1100-CAAA-R7 | U4 | BGA25C40P5X5_207X207X52N |  | $2.23
RT8059GJ5 | RT8059GJ5 | U5 | TSOT-23-5_RIT |  | $0.32
MMBT2222AM3T5G | MMBT2222AM3T5G | U6,U10 | SOT-723_0P85X1P25_ONS-M |  | $0.40
PCM5102 2VRMS DirectPath, 112dB Audio Stereo DAC with 32-bit, 384kHz PCM Interface, TSSOP-20 | PCM5102APWR | U8 | TSSOP-20_4.4x6.5mm_P0.65mm |  | 4.43
PAM8403DR | PAM8403DR | U9 | SOIC127P605X150-16N |  | $0.72
 |  |  |  |  | ~ $62

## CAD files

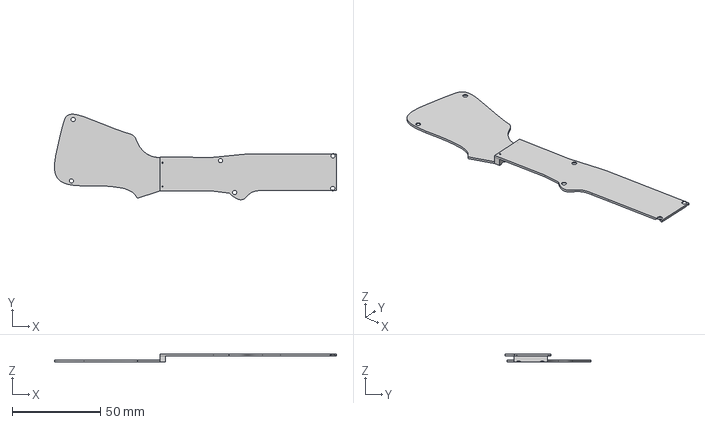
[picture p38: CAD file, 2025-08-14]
CADDesign/Right Enclosure.step
159.5 x 48.4 x 4.50 mm

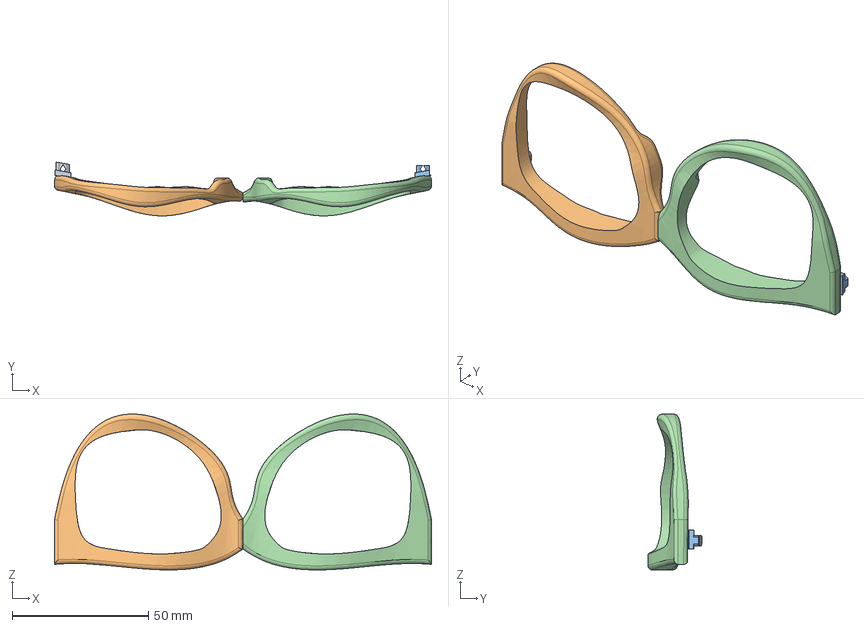
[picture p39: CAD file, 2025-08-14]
CADDesign/Glasses Frame.step
138.6 x 19.8 x 57.3 mm
Hinges
Hinges(Mirror)

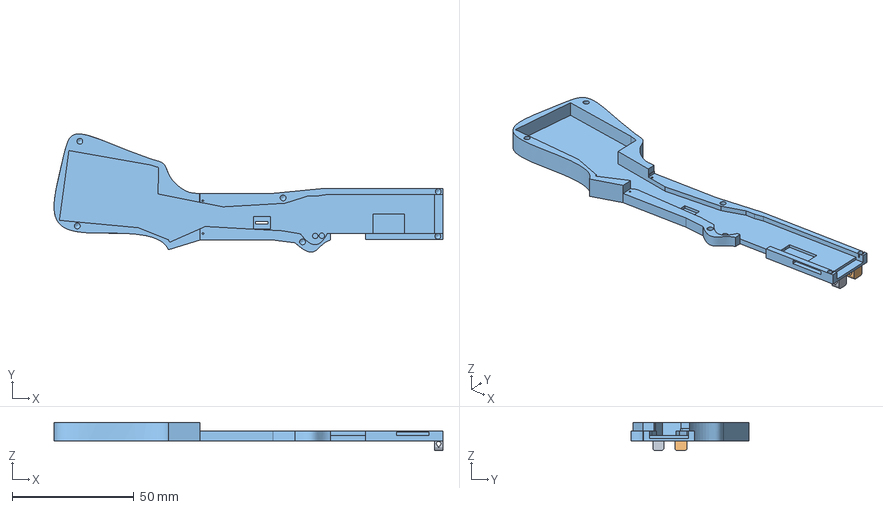
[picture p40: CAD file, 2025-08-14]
CADDesign/Left casing.step
159.5 x 48.4 x 11.5 mm
7.5mm Thickness 1
Hinge 1
Hinge 2

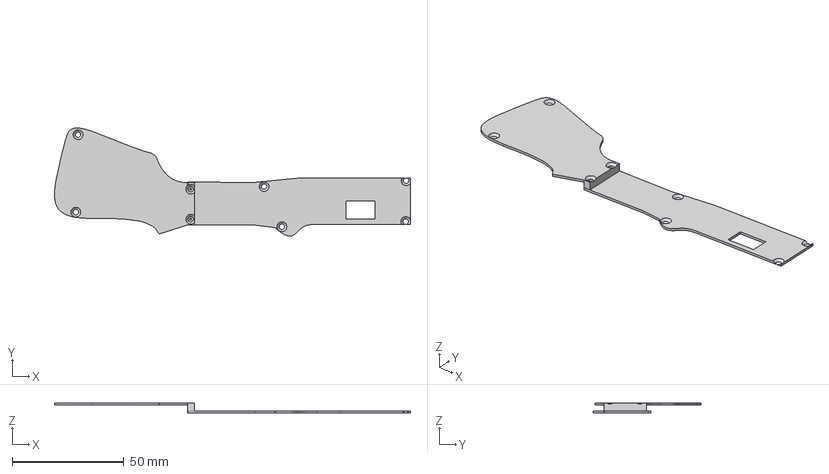
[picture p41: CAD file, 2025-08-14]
CADDesign/left Enclosure.step
159.5 x 48.4 x 4.50 mm

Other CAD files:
CADDesign/Right Casing.step

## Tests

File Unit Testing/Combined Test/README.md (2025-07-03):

# Combined Test (TOF & Audio System Test Using Breadboard)

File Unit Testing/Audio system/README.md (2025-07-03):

# Combined Test (Audio System Test Using Breadboard)

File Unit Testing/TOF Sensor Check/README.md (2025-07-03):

# Combined Test (TOF System Test Using Breadboard)

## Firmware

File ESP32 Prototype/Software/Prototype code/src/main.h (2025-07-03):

#include <stdio.h>
#include <stdint.h>
#include <stdbool.h>

//ESP32 General Libraries
#include "driver/gpio.h"
#include "sdkconfig.h"
#include "esp_log.h"
#include "esp_sleep.h"
#include "esp_timer.h"

//Communication Protocols: UART
#include "driver/uart.h"

//FreeRTOS
#include "freertos/FreeRTOS.h"
#include "freertos/task.h"
#include "freertos/queue.h"

//WIFI
#include "esp_wifi.h"

//Bluetooth
#include "esp_bt.h"


//Error debugging
#define LOG_LOCAL_LEVEL ESP_LOG_VERBOSE
esp_err_t ret;
const char *TAG;


/* Finite State Machine */
typedef enum {
    STATE_IDLE,
    STATE_ALERT,
    STATE_MUTE
} system_state_t;

//IDLE WHEN: Chilling and doing nothing
//ALERT WHEN: Include here the playing the buzzer and stuff
//MUTE WHEN: Interrupt and turn everything off

system_state_t current_state = STATE_IDLE;
#define MUTE_DURATION

/* GPIO PINS */

//INPUT PINS
#define GPIO_INPUT_IO_0 0
#define GPIO_INPUT_IO_15 15
#define GPIO_INPUT_IO_19 19

#define GPIO_INPUT_PIN_SEL  ( (1ULL << GPIO_INPUT_IO_0)  | \
                              (1ULL << GPIO_INPUT_IO_15) | \
                              (1ULL << GPIO_INPUT_IO_19) )

//OUTPUT PINS
#define GPIO_OUTPUT_IO_2 2
#define GPIO_OUTPUT_IO_4 4
#define GPIO_OUTPUT_IO_5 5
#define GPIO_OUTPUT_IO_18 18
#define GPIO_OUTPUT_IO_12 12
#define GPIO_OUTPUT_IO_13 13
#define GPIO_OUTPUT_IO_14 14
#define GPIO_OUTPUT_IO_23 23
#define GPIO_OUTPUT_IO_25 25

#define GPIO_OUTPUT_PIN_SEL  ( (1ULL << GPIO_OUTPUT_IO_2)  | \
                               (1ULL << GPIO_OUTPUT_IO_4)  | \
                               (1ULL << GPIO_OUTPUT_IO_5)  | \
                               (1ULL << GPIO_OUTPUT_IO_12) | \
                               (1ULL << GPIO_OUTPUT_IO_13) | \
                               (1ULL << GPIO_OUTPUT_IO_14) | \
                               (1ULL << GPIO_OUTPUT_IO_18) | \
                               (1ULL << GPIO_OUTPUT_IO_23) | \
                               (1ULL << GPIO_OUTPUT_IO_25) )

                               /* UART Pins */
const uart_port_t uart_port_num = UART_NUM_0;
    
//UART Driver Installation
#define UART_BUFFER_SIZE 2048
QueueHandle_t uart_queue;

#define EVENT_QUEUE_SIZE 10

#define UART_RX_PIN 1 
#define UART_TX_PIN 3

/* I2C Pins */
#include "driver/i2c_master.h"

//Task Handler 
TaskHandle_t write_handler = NULL;
TaskHandle_t read_handler = NULL;

//Handler for read and write operations
i2c_master_dev_handle_t i2c_dev;

#define I2C_MASTER_SCL_IO 22 //SDA Pin
#define I2C_MASTER_SDA_IO 21 //SCL Pin

#define I2C_PORT_NUM_0 I2C_NUM_0
#define I2C_PORT_NUM_1 I2C_NUM_1
#define I2C_TOF_DEFAULT_ADDRESS 0X29
#define I2C_TOF1_ADDRESS 0x30
#define I2C_TOF2_ADDRESS 0x31 

//I2S libraries
#include "driver/i2s_std.h"

//Task handler for playing beeps
TaskHandle_t music_handler = NULL;

#define LRCK_IO 32
#define DOUT_IO 33
#define BCK_IO 27
#define SCK_IO 26

//I2S Constants
#define SAMPLE_RATE 44100

// Beep beep beep   
#define BEEP_FREQ 2000
#define AMPLITUDE 30000
#define DURATION 0.5

//Mapping the beeping sounds
#define THRESHOLD 30

i2s_chan_handle_t tx_handler;

//Distance
volatile uint16_t distance_cm;
int beep_delay;

//Map function constants
#define THRESHOLD 30
#define BUZZER_MAX 250
#define BUZZER_MIN 10 

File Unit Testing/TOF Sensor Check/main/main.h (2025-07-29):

#include "sdkconfig.h"
#include "driver/gpio.h"

#include <stdio.h>
#include <stdint.h>
#include <stdbool.h>

//ESP32 General Libraries
#include "driver/gpio.h"
#include "sdkconfig.h"


#define LOG_LOCAL_LEVEL ESP_LOG_VERBOSE
#include "esp_log.h"


//Communication Protocols: I2C
#include "driver/i2c_master.h"
#include "driver/i2c_slave.h"

//Communication Protocols: UART
#include "driver/uart.h"


//FreeRTOS
#include "freertos/FreeRTOS.h"
#include "freertos/task.h"
#include "freertos/queue.h"


//Error debugging
esp_err_t ret;
const char *TAG;

//Distance
uint16_t distance_cm = 0;

/*
==============================================
==============================================
                 PINS
==============================================
==============================================
*/

/* OUTPUT PINS */
#define GPIO_OUTPUT_IO_23 23

/* UART Pins */
const uart_port_t uart_port_num = UART_NUM_0;

#define UART_RX_PIN 1 
#define UART_TX_PIN 3

//UART Driver Installation
#define UART_TX_SIZE 1024
QueueHandle_t uart_queue;

#define EVENT_QUEUE_SIZE 10


/* I2C Pins */

//The bus handle is like a USB hub maanger,
//all configurations are plugged into this hub
i2c_master_bus_handle_t tof_bus_handle;

//Handler for the specific I2C device (usually a slave) on the I2C bus
i2c_master_dev_handle_t tof_dev_handle;


#define I2C_MASTER_SCL_IO 22 //SDA Pin
#define I2C_MASTER_SDA_IO 21 //SCL Pin

#define I2C_PORT_NUM I2C_NUM_0
#define I2C_TOF_ADDRESS 0x29

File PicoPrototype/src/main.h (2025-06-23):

#include <stdio.h>
#include <stdint.h>
#include <stdbool.h>
#include "pico/stdlib.h" 
#include "hardware/timer.h" //We need to time certain stuff
#include "hardware/gpio.h" //For the buzzer interrupt
#include "hardware/irq.h" //Used for interrupt in order to control PWM
#include "hardware/pwm.h" //Used for driving audio via PWM

#define TRIG_PIN 4
#define ECHO_PIN 5
#define SPEAKER_PIN 17
#define BUZZER_PIN 13

//Wrapval determines how long a PWM cycle should last
#define WRAPVAL 354
//The CLKDIV is for the clock divider in calibrating how
//many cycles can the given freq complete

//In simple terms, it's calibrating the speed of the frequency
#define CLKDIV 8.0f

#define AND &&
#define TIMEOUT 30000

//Map function constants
#define THRESHOLD 30
#define BUZZER_MAX 250
#define BUZZER_MIN 10 

void setup_pins(void);

/* get_pulse: activates the HY-SRF05
* @param a: GPIO pin trig pin is connected 
* @param b: GPIO pin echo pin is connected
* @return: confirmation if successful operation
*/
uint64_t get_pulse(uint8_t trig_pin, uint8_t echo_pin);

/* get_cm: Converts the distance to cm
* @param a: GPIO pin trig pin is connected 
* @param b: GPIO pin echo pin is connected
* @return: the cm result after converting
*/

uint64_t get_cm(uint8_t trig_pin, uint8_t echo_pin);

//Initialize the interrupts of PWM and the buzzzer
void interrupt_initialize();

//Interrupt handler for the buzzer
void buzzer_cook_handler();

//Interrupt handler for the speaker
void pwm_interrupt_handler();

/* map: maps the values of the buzzer delay
* @param a: the distance taken by the ultrasonic sensor
* @param b: the starting range of the current value
* @param c: the ending range of the current value
* @param d: the new minimum target range 
* @param e: the new maximum target range
* @return: integer within the new range
*/
int map(int distance, int starting_low, int starting_high, int ending_low, int ending_high);

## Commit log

2025-06-23 added PCB and CAD
    [combined.gbl, combined.gbo, combined.gbp, combined.gbs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]
2025-06-23 Added csv file
    [Pagtingin_Final_BOM - Pagtingin_Final.csv.csv]
2025-06-23 updated BOM
    [Pagtingin_Final_BOM - Pagtingin_Final.csv]
